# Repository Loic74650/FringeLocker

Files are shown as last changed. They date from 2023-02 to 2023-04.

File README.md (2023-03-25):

# FringeLocker
## Intro
 FringeLocker, as its name indicates, is an electronic system designed to lock interference fringes of an optical interferometer or a holography recording setup.
 The purpose of locking an interferometer is usually to stabilize unstable interference fringes due to mechanical vibrations or thermal drifts.<br />
 Demo video: https://youtu.be/0IrlpE1sPkQ
 
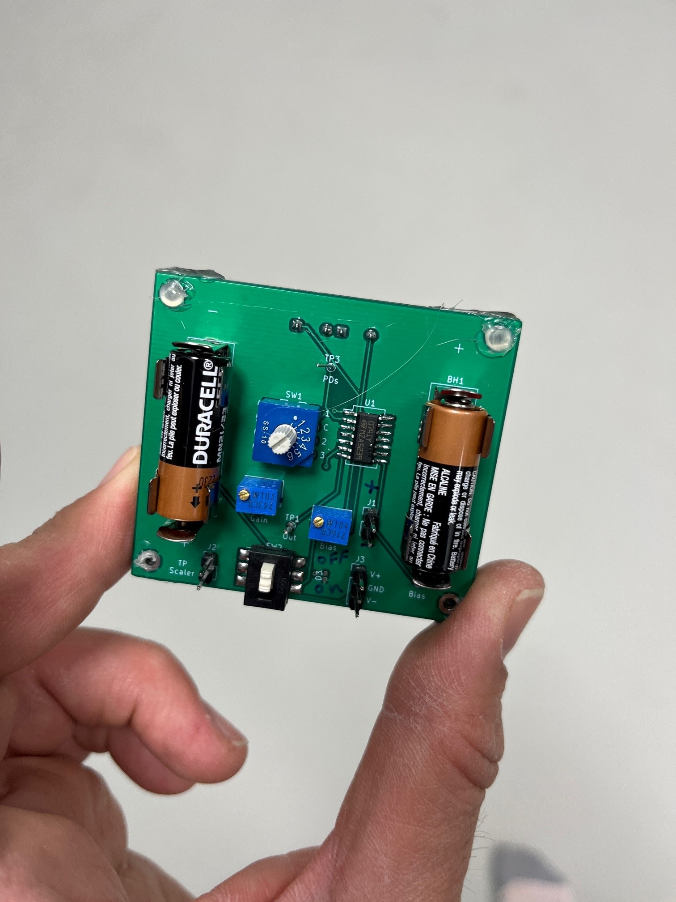
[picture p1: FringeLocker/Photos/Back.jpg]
  <br />
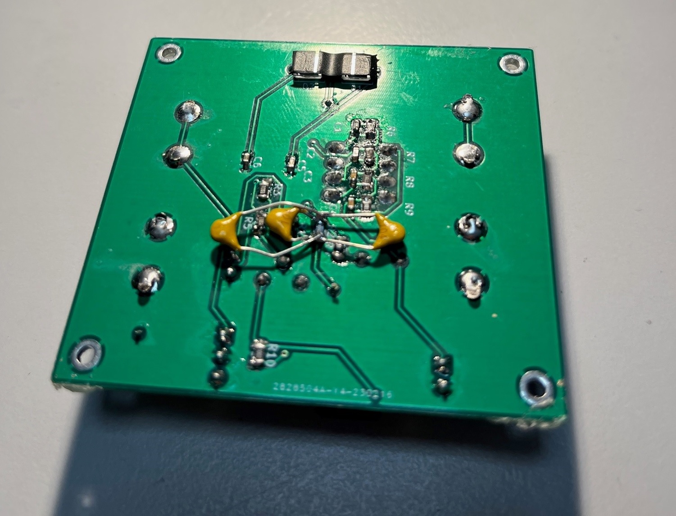
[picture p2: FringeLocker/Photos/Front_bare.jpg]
  <br />
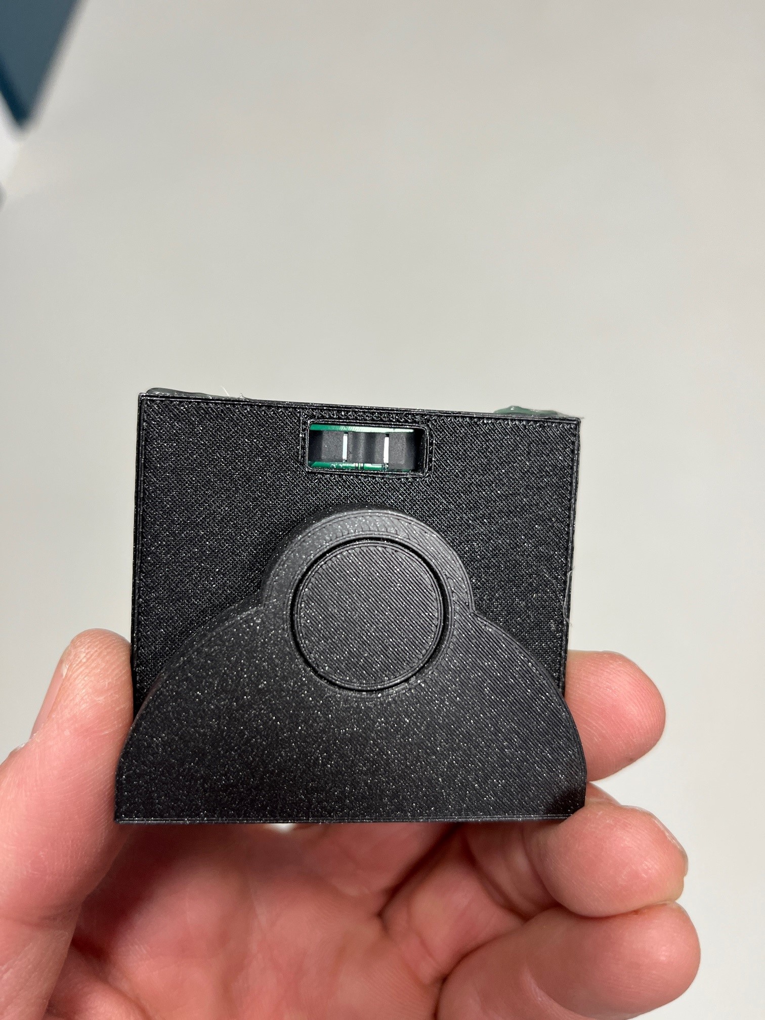
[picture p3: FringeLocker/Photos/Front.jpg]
  <br />
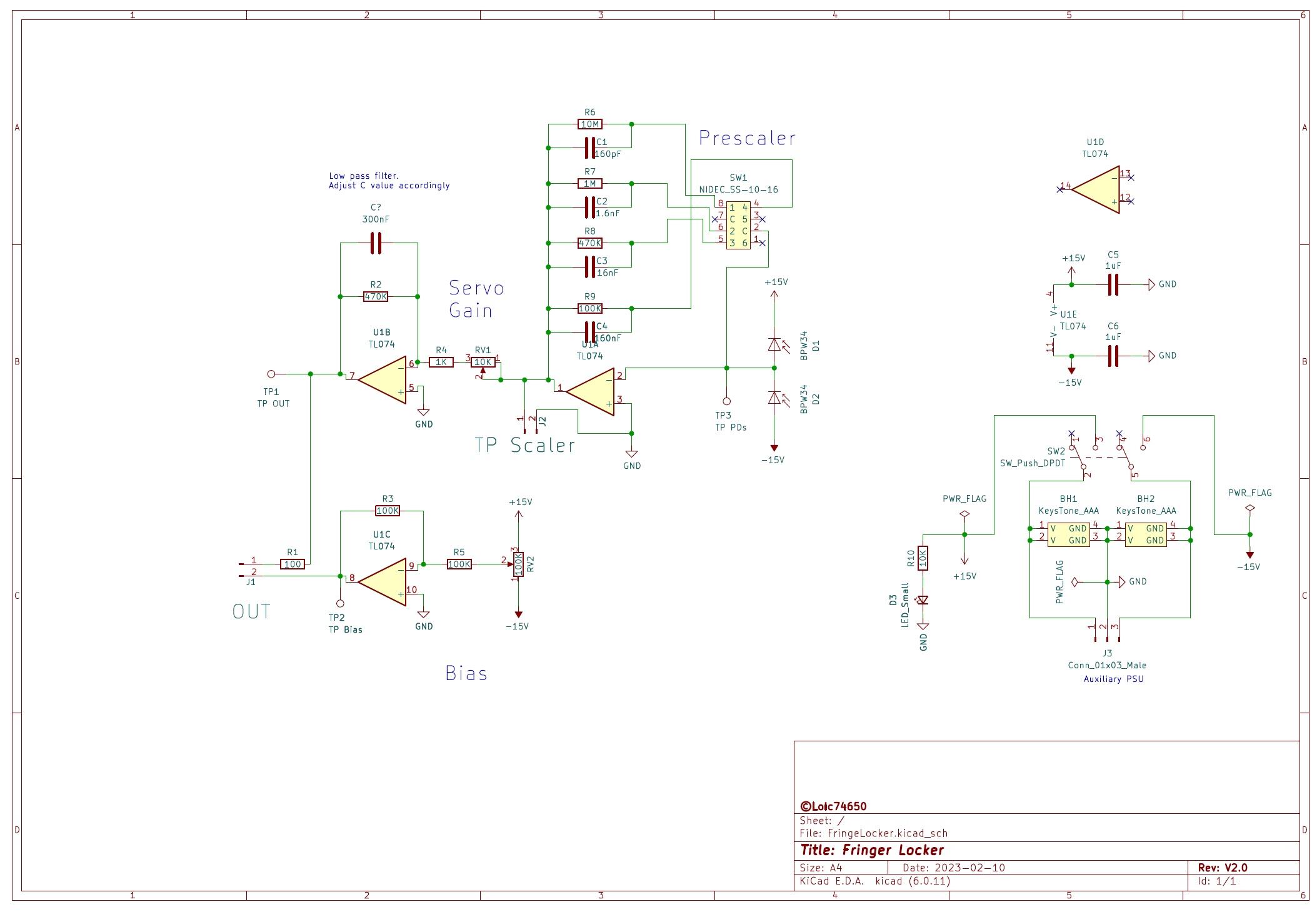
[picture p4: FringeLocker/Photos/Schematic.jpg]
  <br /><br />
 
## Working principle
Two photodiodes sample the interference fringes and detect any movement of those. 
A low noise amplifier and feedback loop drive a mirror which is placed on a piezo transducer in order to move one arm of the interferometer and compensate for the detected fringe movements

## Setup
This version of FringeLocker is powered by two MN21/A23 12V batteries. Alternatively connector J3 on the board can be used to power the board with an external supply of
your choice (remove the batteries first!). The board accepts supply voltages up to +/-18Volts and so currently I am using two 9V batteries in series for each voltage ramp in order to increase lifetime on battery.
The photodiodes need to be masked of, leaving just one slit 0.5mm wide per photodiode. See image in the photos folder.<br />
Slider switch SW2 switched ON/OFF the board.  
There are three adjustments to be performed on the board. 

1- Servo Gain
RV1 10 turns potentiometer adjusts the servo gain. Start by adjusting it to minimum

2- Output bias
RV2 10 turns potentiometer adjusts the level of bias voltage to the piezo transducer. Since positive or negative voltages can be applied to the transducer it is necessary to apply
a bias to it. Use a voltmeter to measure the bias voltage between ground (the pcb mounting holes in each corner are grounded) and Test Point 2 (TP2 or TP Bias) and adjust it to 18 volts or so.

3- PresScaler switch
SW1 is a rotary switch which selects a preamplification of the photodiodes signal with various gains. Start by adjusting it to minimum

## Servo loop adjustment
Place the photodiodes within interference fringes of the interferometer. Adjust the interference fringes spacing so that their spacing is approximately 15mm (twice the spacing between the photodiodes). 
Power the board and start with the lowest gain on the PreScaler switch SW1 and move to larger gains incrementally until the feedback loop starts oscillating.
Revert to the previous gain setting in order to stop the oscillation. You can then fine adjust the loop gain RV1 by increasing it slowly until the loop starts oscillating, then reverting a bit to stop the oscillation.

## Bugs
An unpolarized 100nF capacitor needs to be manually added in parallel with R2 in order to create an active low pass filter and prevent the feedback loop from oscillating

## Credits
Thanks to Phil Hobbs for his help on the schematic design

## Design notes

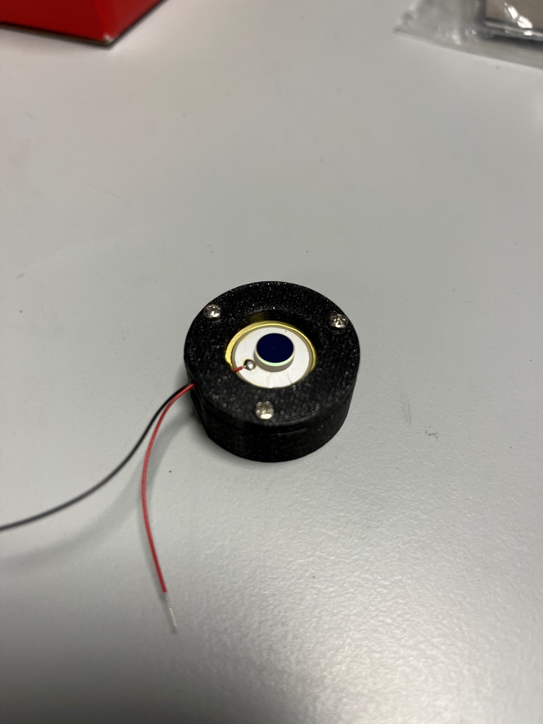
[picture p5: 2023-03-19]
FringeLocker/Photos/FL_6.jpg

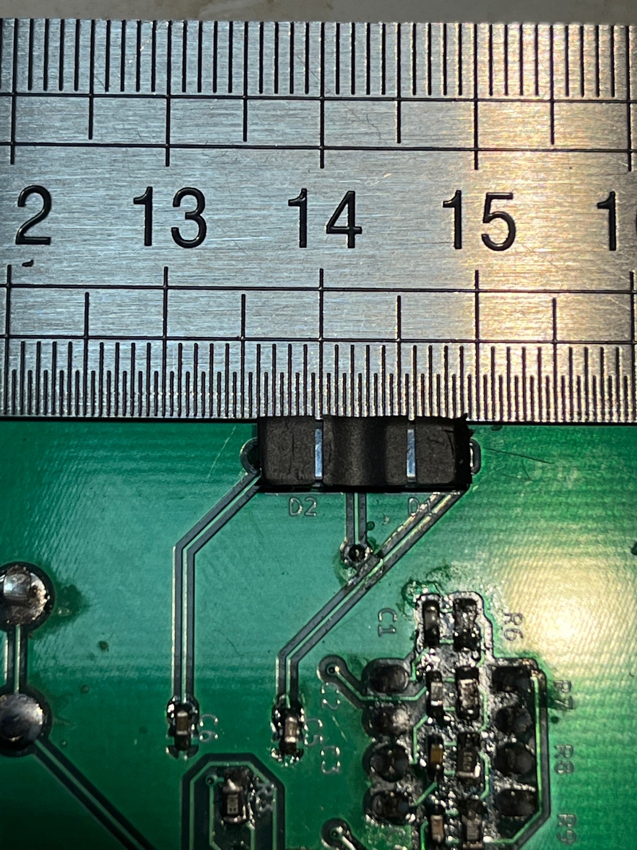
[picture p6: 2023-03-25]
FringeLocker/Photos/PDs_masks.jpg

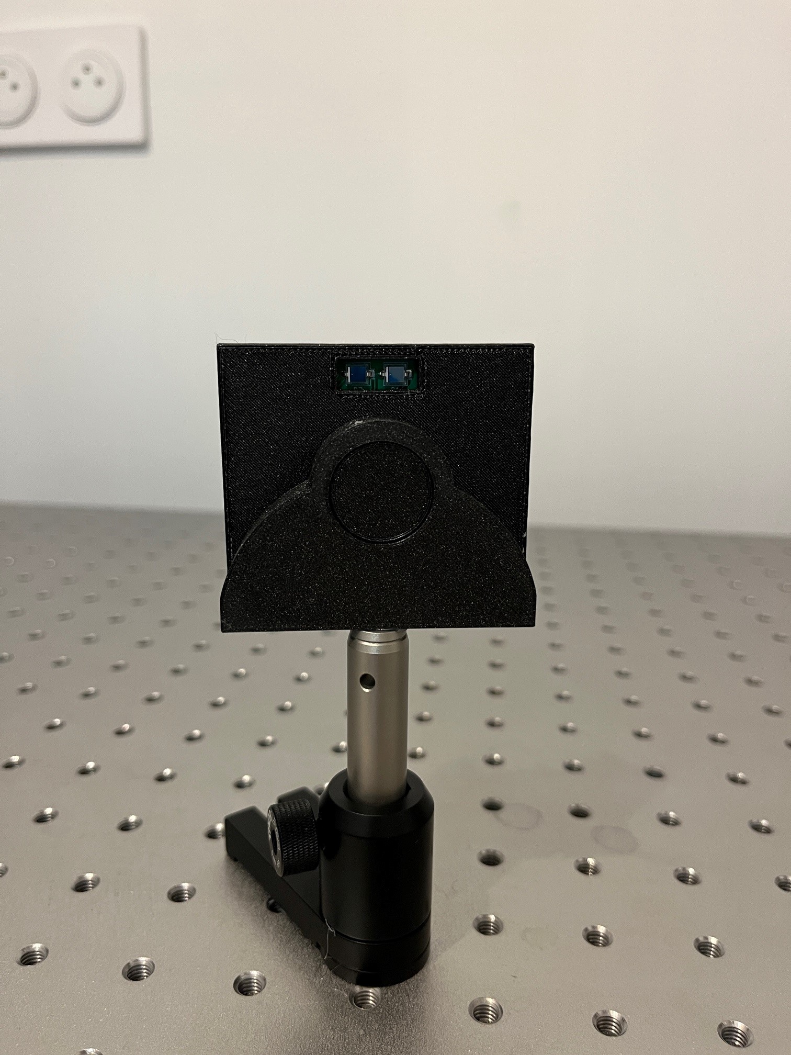
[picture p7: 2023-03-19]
FringeLocker/Photos/FL_1.jpg

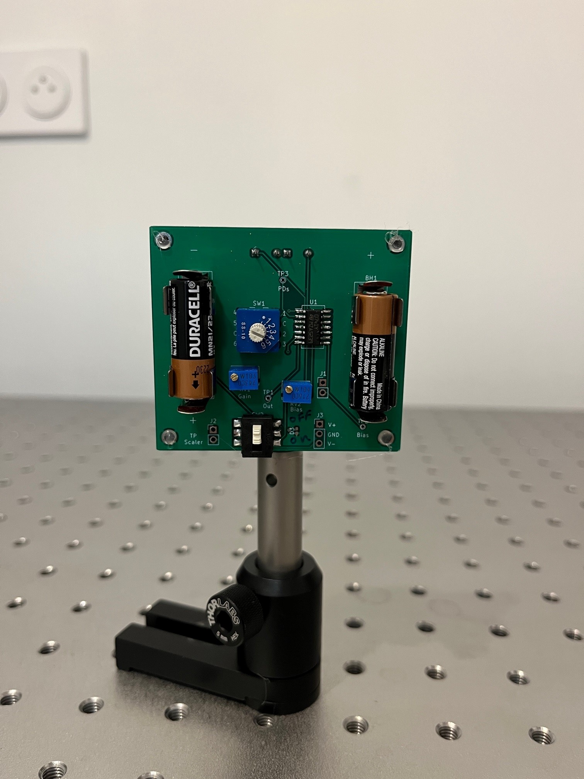
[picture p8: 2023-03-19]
FringeLocker/Photos/FL_2.jpg

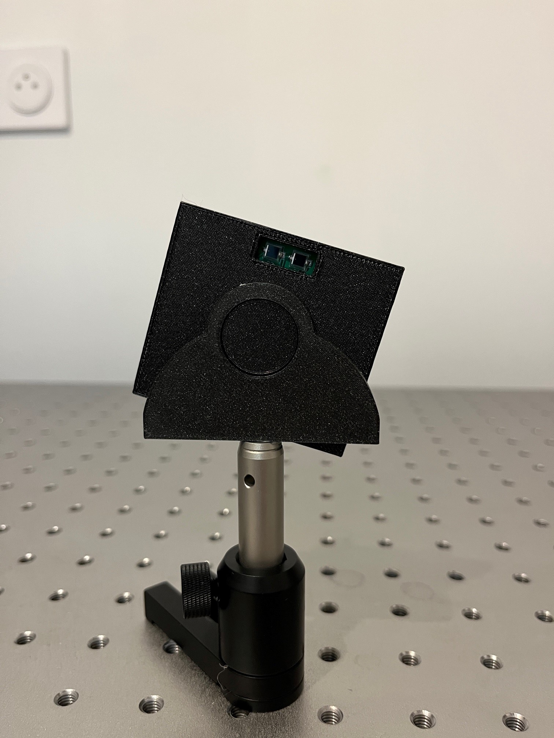
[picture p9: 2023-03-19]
FringeLocker/Photos/FL_3.jpg

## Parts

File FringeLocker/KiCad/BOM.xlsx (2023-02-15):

Column1 | Column2 | Column3 | Column4 | Column5 | Column6 | Column7 | Column8 | Column10
Source: | C:\Users\USER\Documents\GitHub\FringeLocker\FringeLocker\FringeLocker.kicad_sch
Date: | 15/02/2023 15:58:59
Tool: | Eeschema (6.0.11)
Generator: | C:\Program Files\KiCad\6.0\bin\scripting\plugins/bom_csv_grouped_by_value.py
Component Count: | 32
Individual Components:
Item | Qty | Reference(s) | Value | LibPart | Footprint | Datasheet | Unit price (€) | Total price (€)
 |  | BH1 | KeysTone_AAA | My_Library:KeysTone_AAA | BatteryHolder:Keystone_AAA
 |  | BH2 | KeysTone_AAA | My_Library:KeysTone_AAA | BatteryHolder:Keystone_AAA
 |  | C1 | 160pF | Device:C | Capacitor_SMD:C_0603_1608Metric_Pad1.08x0.95mm_HandSolder | ~
 |  | C2 | 1.6nF | Device:C | Capacitor_SMD:C_0603_1608Metric_Pad1.08x0.95mm_HandSolder | ~
 |  | C3 | 16nF | Device:C | Capacitor_SMD:C_0603_1608Metric_Pad1.08x0.95mm_HandSolder | ~
 |  | C4 | 160nF | Device:C | Capacitor_SMD:C_0603_1608Metric_Pad1.08x0.95mm_HandSolder | ~
 |  | C5 | 1uF | Device:C | Capacitor_SMD:C_0603_1608Metric_Pad1.08x0.95mm_HandSolder | ~
 |  | C6 | 1uF | Device:C | Capacitor_SMD:C_0603_1608Metric_Pad1.08x0.95mm_HandSolder | ~
 |  | D1 | BPW34 | Sensor_Optical:BPW34 | OptoDevice:Osram_DIL2_4.3x4.65mm_P5.08mm | http://www.vishay.com/docs/81521/bpw34.pdf
 |  | D2 | BPW34 | Sensor_Optical:BPW34 | OptoDevice:Osram_DIL2_4.3x4.65mm_P5.08mm | http://www.vishay.com/docs/81521/bpw34.pdf
 |  | D3 | LED_Small | Device:LED_Small | LED_SMD:LED_0402_1005Metric_Pad0.77x0.64mm_HandSolder | ~
 |  | J1 | OUT | Connector:Conn_01x02_Male | Connector_PinHeader_2.54mm:PinHeader_1x02_P2.54mm_Vertical | ~
 |  | J2 | TP Scaler | Connector:Conn_01x02_Male | Connector_PinHeader_2.54mm:PinHeader_1x02_P2.54mm_Vertical | ~
 |  | J3 | Conn_01x03_Male | Connector:Conn_01x03_Male | Connector_PinHeader_2.54mm:PinHeader_1x03_P2.54mm_Vertical | ~
 |  | R1 | 100 | Device:R | Resistor_SMD:R_0805_2012Metric_Pad1.20x1.40mm_HandSolder | ~
 |  | R2 | 22K | Device:R | Resistor_SMD:R_0805_2012Metric_Pad1.20x1.40mm_HandSolder | ~
 |  | R3 | 100K | Device:R | Resistor_SMD:R_0805_2012Metric_Pad1.20x1.40mm_HandSolder | ~
 |  | R4 | 1K | Device:R | Resistor_SMD:R_0805_2012Metric_Pad1.20x1.40mm_HandSolder | ~
 |  | R5 | 100K | Device:R | Resistor_SMD:R_0805_2012Metric_Pad1.20x1.40mm_HandSolder | ~
 |  | R6 | 1M | Device:R | Resistor_SMD:R_0805_2012Metric_Pad1.20x1.40mm_HandSolder | ~
 |  | R7 | 100K | Device:R | Resistor_SMD:R_0805_2012Metric_Pad1.20x1.40mm_HandSolder | ~
 |  | R8 | 10K | Device:R | Resistor_SMD:R_0805_2012Metric_Pad1.20x1.40mm_HandSolder | ~
 |  | R9 | 1K | Device:R | Resistor_SMD:R_0805_2012Metric_Pad1.20x1.40mm_HandSolder | ~
 |  | R10 | 10K | Device:R | Resistor_SMD:R_0805_2012Metric_Pad1.20x1.40mm_HandSolder | ~
 |  | RV1 | 10K | FringeLocker-rescue:R_POT-Device | Potentiometer_THT:Potentiometer_Bourns_3266W_Vertical
 |  | RV2 | 100K | FringeLocker-rescue:R_POT-Device | Potentiometer_THT:Potentiometer_Bourns_3266W_Vertical
 |  | SW1 | NIDEC_SS-10-16 | My_Library:NIDEC_SS-10-16 | BatteryHolder:NIDEC_SS-10-16
 |  | SW2 | SW_Push_DPDT | Switch:SW_Push_DPDT | BatteryHolder:SlideSwitchASE_DPDT | ~
 |  | TP1 | TP OUT | Connector:TestPoint | TestPoint:TestPoint_THTPad_D1.0mm_Drill0.5mm | ~
 |  | TP2 | TP Bias | Connector:TestPoint | TestPoint:TestPoint_THTPad_D1.0mm_Drill0.5mm | ~
 |  | TP3 | TP PDs | Connector:TestPoint | TestPoint:TestPoint_THTPad_D1.0mm_Drill0.5mm | ~
 |  | U1 | TL074 | Amplifier_Operational:TL074 | Package_SO:SO-14_5.3x10.2mm_P1.27mm | http://www.ti.com/lit/ds/symlink/tl071.pdf
Collated Components:
Item | Qty | Reference(s) | Value | LibPart | Footprint | Datasheet | Unit price (€) | Total price (€)
1 | 2 | BH1, BH2 | KeysTone_AAA | My_Library:KeysTone_AAA | BatteryHolder:Keystone_AAA |  | 0.38 | 0.76
2 | 1 | C1 | 160pF | Device:C | Capacitor_SMD:C_0603_1608Metric_Pad1.08x0.95mm_HandSolder | ~ | 0.1 | 0.1
3 | 1 | C2 | 1.6nF | Device:C | Capacitor_SMD:C_0603_1608Metric_Pad1.08x0.95mm_HandSolder | ~ | 0.1 | 0.1
4 | 1 | C3 | 16nF | Device:C | Capacitor_SMD:C_0603_1608Metric_Pad1.08x0.95mm_HandSolder | ~ | 0.1 | 0.1
5 | 1 | C4 | 160nF | Device:C | Capacitor_SMD:C_0603_1608Metric_Pad1.08x0.95mm_HandSolder | ~ | 0.1 | 0.1
6 | 2 | C5, C6 | 1uF | Device:C | Capacitor_SMD:C_0603_1608Metric_Pad1.08x0.95mm_HandSolder | ~ | 0.1 | 0.2
7 | 2 | D1, D2 | BPW34 | Sensor_Optical:BPW34 | OptoDevice:Osram_DIL2_4.3x4.65mm_P5.08mm | http://www.vishay.com/docs/81521/bpw34.pdf | 0.68 | 1.36
8 | 1 | D3 | LED_Small | Device:LED_Small | LED_SMD:LED_0402_1005Metric_Pad0.77x0.64mm_HandSolder | ~ | 0.43 | 0.43
9 | 1 | J1 | OUT | Connector:Conn_01x02_Male | Connector_PinHeader_2.54mm:PinHeader_1x02_P2.54mm_Vertical | ~ | 0.1 | 0.1
10 | 1 | J2 | TP Scaler | Connector:Conn_01x02_Male | Connector_PinHeader_2.54mm:PinHeader_1x02_P2.54mm_Vertical | ~ | 0.1 | 0.1
11 | 1 | J3 | Conn_01x03_Male | Connector:Conn_01x03_Male | Connector_PinHeader_2.54mm:PinHeader_1x03_P2.54mm_Vertical | ~ | 0.1 | 0.1
12 | 1 | R1 | 100 | Device:R | Resistor_SMD:R_0805_2012Metric_Pad1.20x1.40mm_HandSolder | ~ | 0.1 | 0.1
13 | 1 | R2 | 22K | Device:R | Resistor_SMD:R_0805_2012Metric_Pad1.20x1.40mm_HandSolder | ~ | 0.1 | 0.1
14 | 3 | R3, R5, R7 | 100K | Device:R | Resistor_SMD:R_0805_2012Metric_Pad1.20x1.40mm_HandSolder | ~ | 0.1 | 0.3
15 | 2 | R4, R9 | 1K | Device:R | Resistor_SMD:R_0805_2012Metric_Pad1.20x1.40mm_HandSolder | ~ | 0.1 | 0.2
16 | 1 | R6 | 1M | Device:R | Resistor_SMD:R_0805_2012Metric_Pad1.20x1.40mm_HandSolder | ~ | 0.1 | 0.1
17 | 2 | R8, R10 | 10K | Device:R | Resistor_SMD:R_0805_2012Metric_Pad1.20x1.40mm_HandSolder | ~ | 0.1 | 0.2
18 | 1 | RV1 | 10K | FringeLocker-rescue:R_POT-Device | Potentiometer_THT:Potentiometer_Bourns_3266W_Vertical |  | 2.49 | 2.49
19 | 1 | RV2 | 100K | FringeLocker-rescue:R_POT-Device | Potentiometer_THT:Potentiometer_Bourns_3266W_Vertical |  | 4.19 | 4.19
20 | 1 | SW1 | NIDEC_SS-10-16 | My_Library:NIDEC_SS-10-16 | BatteryHolder:NIDEC_SS-10-16 |  | 3.88 | 3.88
21 | 1 | SW2 | SW_Push_DPDT | Switch:SW_Push_DPDT | BatteryHolder:SlideSwitchASE_DPDT | ~ | 5.03 | 5.03
22 | 1 | TP1 | TP OUT | Connector:TestPoint | TestPoint:TestPoint_THTPad_D1.0mm_Drill0.5mm | ~ | 0 | 0
23 | 1 | TP2 | TP Bias | Connector:TestPoint | TestPoint:TestPoint_THTPad_D1.0mm_Drill0.5mm | ~ | 0 | 0
24 | 1 | TP3 | TP PDs | Connector:TestPoint | TestPoint:TestPoint_THTPad_D1.0mm_Drill0.5mm | ~ | 0 | 0
25 | 1 | U1 | TL074 | Amplifier_Operational:TL074 | Package_SO:SO-14_5.3x10.2mm_P1.27mm | http://www.ti.com/lit/ds/symlink/tl071.pdf | 0.84 | 0.84
 |  |  |  |  |  |  |  | 0
 |  |  |  |  |  |  |  | 0
 |  |  |  |  |  |  |  | 0
 | 1 | PCB |  | JLCPCB |  | JLPCB | 5 | 5
 |  |  |  |  |  |  | TOTAL | 25.88

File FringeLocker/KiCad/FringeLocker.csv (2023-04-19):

Source: | C:\Users\USER\Documents\GitHub\FringeLocker\FringeLocker\KiCad\FringeLocker.kicad_sch
Date: | 19/04/2023 18:29:47
Tool: | Eeschema (6.0.11)
Generator: | C:\Program Files\KiCad\6.0\bin\scripting\plugins/bom_csv_grouped_by_value.py
Component Count: | 32
Individual Components:
Item | Qty | Reference(s) | Value | LibPart | Footprint | Datasheet
 |  | C1 | 1.6nF | Device:C | Capacitor_SMD:C_0603_1608Metric_Pad1.08x0.95mm_HandSolder | ~
 |  | C2 | 10uF | Device:C | Capacitor_SMD:C_0603_1608Metric_Pad1.08x0.95mm_HandSolder | ~
 |  | C3 | 10uF | Device:C | Capacitor_SMD:C_0603_1608Metric_Pad1.08x0.95mm_HandSolder | ~
 |  | C5 | 1uF | Device:C | Capacitor_SMD:C_0603_1608Metric_Pad1.08x0.95mm_HandSolder | ~
 |  | C6 | 1uF | Device:C | Capacitor_SMD:C_0603_1608Metric_Pad1.08x0.95mm_HandSolder | ~
 |  | D1 | BPW34 | Sensor_Optical:BPW34 | OptoDevice:Osram_DIL2_4.3x4.65mm_P5.08mm | http://www.vishay.com/docs/81521/bpw34.pdf
 |  | D2 | BPW34 | Sensor_Optical:BPW34 | OptoDevice:Osram_DIL2_4.3x4.65mm_P5.08mm | http://www.vishay.com/docs/81521/bpw34.pdf
 |  | D3 | LED_Small | Device:LED_Small | LED_SMD:LED_0402_1005Metric_Pad0.77x0.64mm_HandSolder | ~
 |  | J1 | OUT | Connector:Conn_01x02_Male | Connector_PinHeader_2.54mm:PinHeader_1x02_P2.54mm_Vertical | ~
 |  | J2 | TP Scaler | Connector:Conn_01x02_Male | Connector_PinHeader_2.54mm:PinHeader_1x02_P2.54mm_Vertical | ~
 |  | J3 | Conn_01x03_Male | Connector:Conn_01x03_Male | Connector_PinHeader_2.54mm:PinHeader_1x03_P2.54mm_Vertical | ~
 |  | R1 | 100 | Device:R | Resistor_SMD:R_0805_2012Metric_Pad1.20x1.40mm_HandSolder | ~
 |  | R2 | 250K | Device:R | Resistor_SMD:R_0805_2012Metric_Pad1.20x1.40mm_HandSolder | ~
 |  | R3 | 100K | Device:R | Resistor_SMD:R_0805_2012Metric_Pad1.20x1.40mm_HandSolder | ~
 |  | R4 | 1K | Device:R | Resistor_SMD:R_0805_2012Metric_Pad1.20x1.40mm_HandSolder | ~
 |  | R5 | 100K | Device:R | Resistor_SMD:R_0805_2012Metric_Pad1.20x1.40mm_HandSolder | ~
 |  | R6 | 1M | Device:R | Resistor_SMD:R_0805_2012Metric_Pad1.20x1.40mm_HandSolder | ~
 |  | R7 | 200 | Device:R | Resistor_SMD:R_0805_2012Metric_Pad1.20x1.40mm_HandSolder | ~
 |  | R8 | 200 | Device:R | Resistor_SMD:R_0805_2012Metric_Pad1.20x1.40mm_HandSolder | ~
 |  | R9 | 10K | Device:R | Resistor_SMD:R_0805_2012Metric_Pad1.20x1.40mm_HandSolder | ~
 |  | R10 | 7.5K | Device:R | Resistor_SMD:R_0805_2012Metric_Pad1.20x1.40mm_HandSolder | ~
 |  | R11 | 1K | Device:R | Resistor_SMD:R_0805_2012Metric_Pad1.20x1.40mm_HandSolder | ~
 |  | RV1 | 3310Y_001_503L | Bourns3310:3310Y | Bourns_3310H:Bourns3310Y
 |  | RV2 | 100K | FringeLocker-rescue:R_POT-Device | Potentiometer_THT:Potentiometer_Bourns_3266W_Vertical
 |  | RV3 | 3310H_001_102L | Bourns3310:Bourns3310H_2 | Bourns_3310H:Bourns3310H
 |  | RV4 | 10K | FringeLocker-rescue:R_POT-Device | Potentiometer_THT:Potentiometer_Bourns_3266W_Vertical
 |  | SW1 | SW_Push_DPDT | Switch:SW_Push_DPDT | BatteryHolder:SlideSwitchASE_DPDT | ~
 |  | TP1 | TP OUT | Connector:TestPoint | TestPoint:TestPoint_THTPad_D1.0mm_Drill0.5mm | ~
 |  | TP2 | TP Bias | Connector:TestPoint | TestPoint:TestPoint_THTPad_D1.0mm_Drill0.5mm | ~
 |  | TP3 | TP PDs | Connector:TestPoint | TestPoint:TestPoint_THTPad_D1.0mm_Drill0.5mm | ~
 |  | U1 | TL074 | Amplifier_Operational:TL074 | Package_SO:SO-14_5.3x10.2mm_P1.27mm | http://www.ti.com/lit/ds/symlink/tl071.pdf
 |  | U2 | TL074 | Amplifier_Operational:TL074 | Package_SO:SO-14_5.3x10.2mm_P1.27mm | http://www.ti.com/lit/ds/symlink/tl071.pdf
Collated Components:
Item | Qty | Reference(s) | Value | LibPart | Footprint | Datasheet
1 | 1 | C1 | 1.6nF | Device:C | Capacitor_SMD:C_0603_1608Metric_Pad1.08x0.95mm_HandSolder | ~
2 | 2 | C2, C3 | 10uF | Device:C | Capacitor_SMD:C_0603_1608Metric_Pad1.08x0.95mm_HandSolder | ~
3 | 2 | C5, C6 | 1uF | Device:C | Capacitor_SMD:C_0603_1608Metric_Pad1.08x0.95mm_HandSolder | ~
4 | 2 | D1, D2 | BPW34 | Sensor_Optical:BPW34 | OptoDevice:Osram_DIL2_4.3x4.65mm_P5.08mm | http://www.vishay.com/docs/81521/bpw34.pdf
5 | 1 | D3 | LED_Small | Device:LED_Small | LED_SMD:LED_0402_1005Metric_Pad0.77x0.64mm_HandSolder | ~
6 | 1 | J1 | OUT | Connector:Conn_01x02_Male | Connector_PinHeader_2.54mm:PinHeader_1x02_P2.54mm_Vertical | ~
7 | 1 | J2 | TP Scaler | Connector:Conn_01x02_Male | Connector_PinHeader_2.54mm:PinHeader_1x02_P2.54mm_Vertical | ~
8 | 1 | J3 | Conn_01x03_Male | Connector:Conn_01x03_Male | Connector_PinHeader_2.54mm:PinHeader_1x03_P2.54mm_Vertical | ~
9 | 1 | R1 | 100 | Device:R | Resistor_SMD:R_0805_2012Metric_Pad1.20x1.40mm_HandSolder | ~
10 | 1 | R2 | 250K | Device:R | Resistor_SMD:R_0805_2012Metric_Pad1.20x1.40mm_HandSolder | ~
11 | 2 | R3, R5 | 100K | Device:R | Resistor_SMD:R_0805_2012Metric_Pad1.20x1.40mm_HandSolder | ~
12 | 2 | R4, R11 | 1K | Device:R | Resistor_SMD:R_0805_2012Metric_Pad1.20x1.40mm_HandSolder | ~
13 | 1 | R6 | 1M | Device:R | Resistor_SMD:R_0805_2012Metric_Pad1.20x1.40mm_HandSolder | ~
14 | 2 | R7, R8 | 200 | Device:R | Resistor_SMD:R_0805_2012Metric_Pad1.20x1.40mm_HandSolder | ~
15 | 1 | R9 | 10K | Device:R | Resistor_SMD:R_0805_2012Metric_Pad1.20x1.40mm_HandSolder | ~
16 | 1 | R10 | 7.5K | Device:R | Resistor_SMD:R_0805_2012Metric_Pad1.20x1.40mm_HandSolder | ~
17 | 1 | RV1 | 3310Y_001_503L | Bourns3310:3310Y | Bourns_3310H:Bourns3310Y
18 | 1 | RV2 | 100K | FringeLocker-rescue:R_POT-Device | Potentiometer_THT:Potentiometer_Bourns_3266W_Vertical
19 | 1 | RV3 | 3310H_001_102L | Bourns3310:Bourns3310H_2 | Bourns_3310H:Bourns3310H
20 | 1 | RV4 | 10K | FringeLocker-rescue:R_POT-Device | Potentiometer_THT:Potentiometer_Bourns_3266W_Vertical
21 | 1 | SW1 | SW_Push_DPDT | Switch:SW_Push_DPDT | BatteryHolder:SlideSwitchASE_DPDT | ~
22 | 1 | TP1 | TP OUT | Connector:TestPoint | TestPoint:TestPoint_THTPad_D1.0mm_Drill0.5mm | ~
23 | 1 | TP2 | TP Bias | Connector:TestPoint | TestPoint:TestPoint_THTPad_D1.0mm_Drill0.5mm | ~
24 | 1 | TP3 | TP PDs | Connector:TestPoint | TestPoint:TestPoint_THTPad_D1.0mm_Drill0.5mm | ~
25 | 2 | U1, U2 | TL074 | Amplifier_Operational:TL074 | Package_SO:SO-14_5.3x10.2mm_P1.27mm | http://www.ti.com/lit/ds/symlink/tl071.pdf

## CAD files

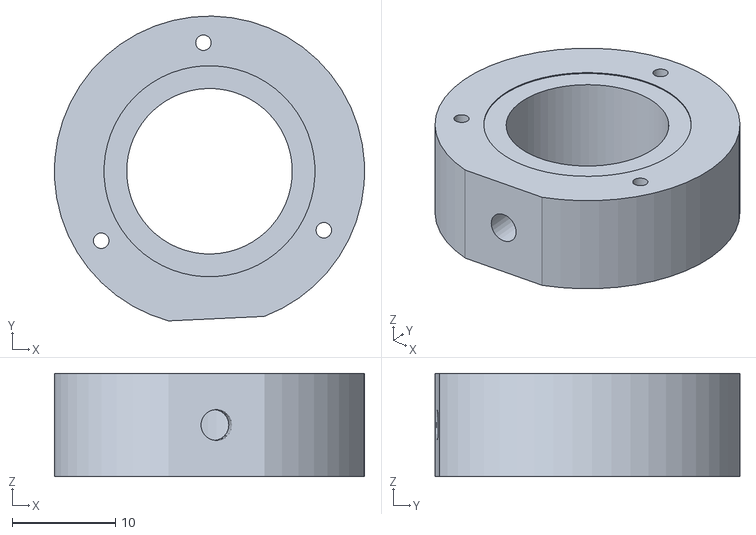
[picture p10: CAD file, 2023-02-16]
FringeLocker/3D Files/SupportPiezoDisc.stl
30.0 x 29.5 x 10.0

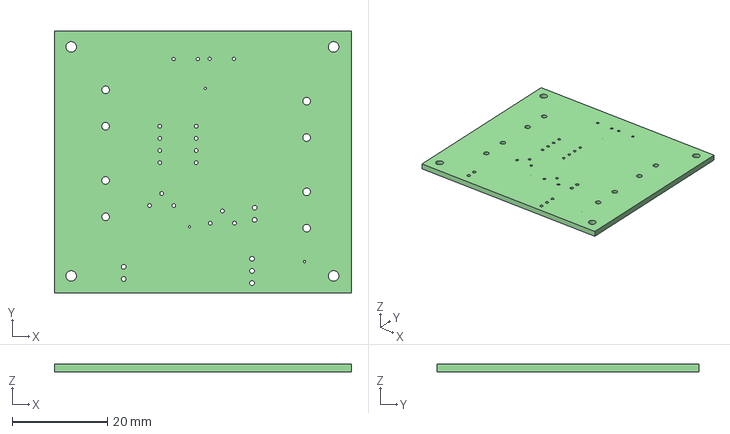
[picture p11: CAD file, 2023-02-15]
FringeLocker/KiCad/FringeLocker.step
62.2 x 54.9 x 1.60 mm

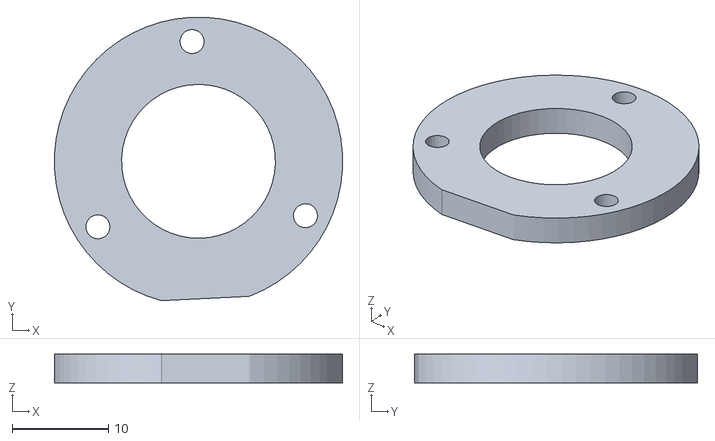
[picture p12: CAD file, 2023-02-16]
FringeLocker/3D Files/ClampPiezoDisc.stl
30.0 x 29.5 x 3.00

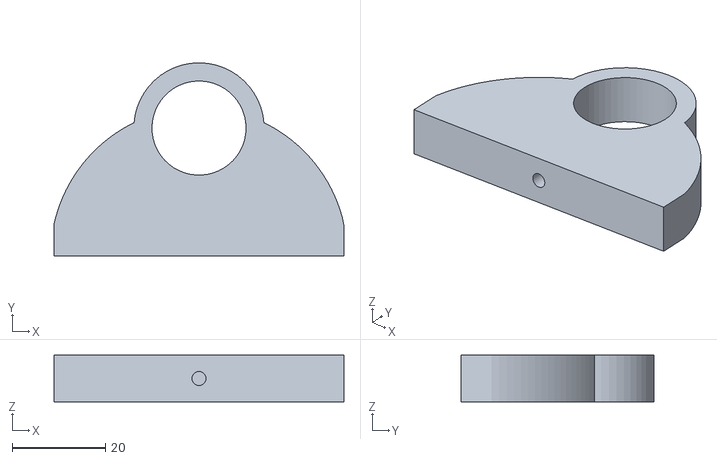
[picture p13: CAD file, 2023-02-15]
FringeLocker/3D Files/SupportPost.stl
62.2 x 41.5 x 10.0

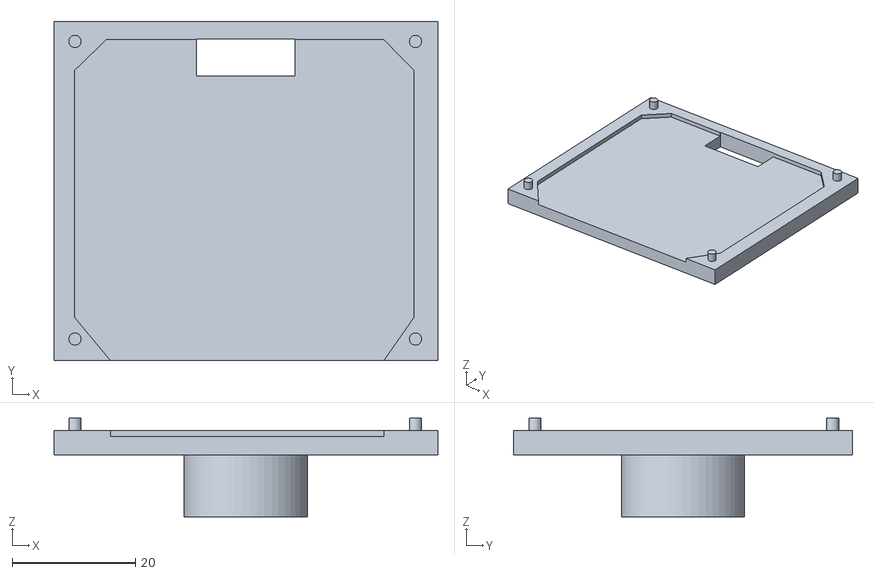
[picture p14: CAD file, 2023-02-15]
FringeLocker/3D Files/SupportPCB.stl
62.2 x 55.0 x 16.0

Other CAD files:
FringeLocker/3D Files/PCBHolderAssembly.skp
FringeLocker/3D Files/PiezoAssembly.skp

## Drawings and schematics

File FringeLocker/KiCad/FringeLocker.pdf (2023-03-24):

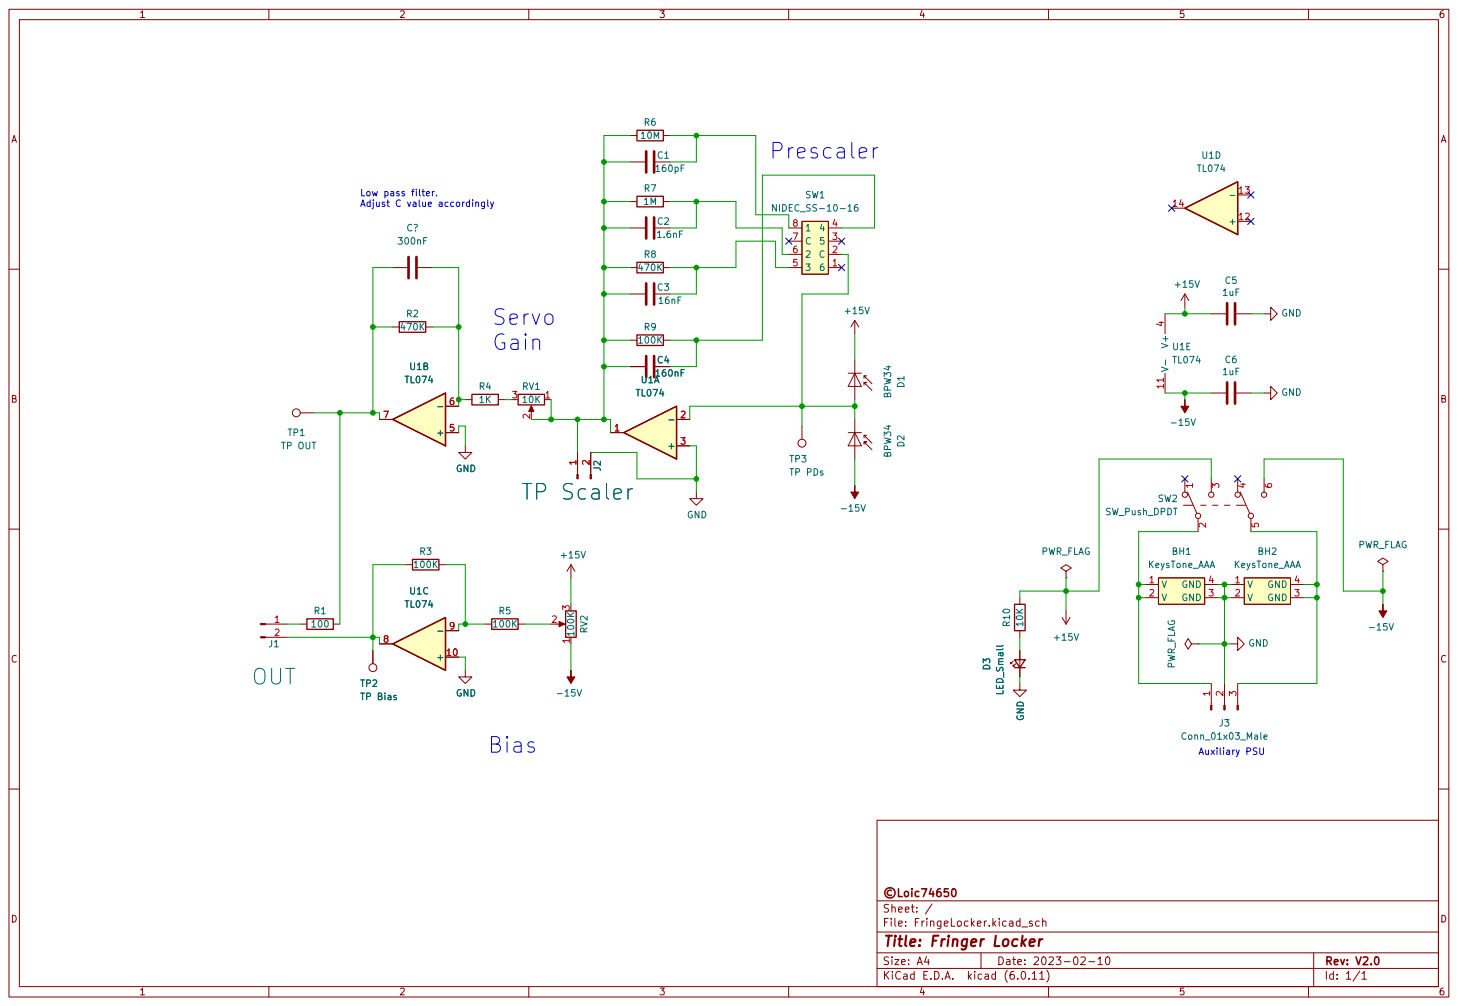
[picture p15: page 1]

Low pass filter. Adjust C value accordingly

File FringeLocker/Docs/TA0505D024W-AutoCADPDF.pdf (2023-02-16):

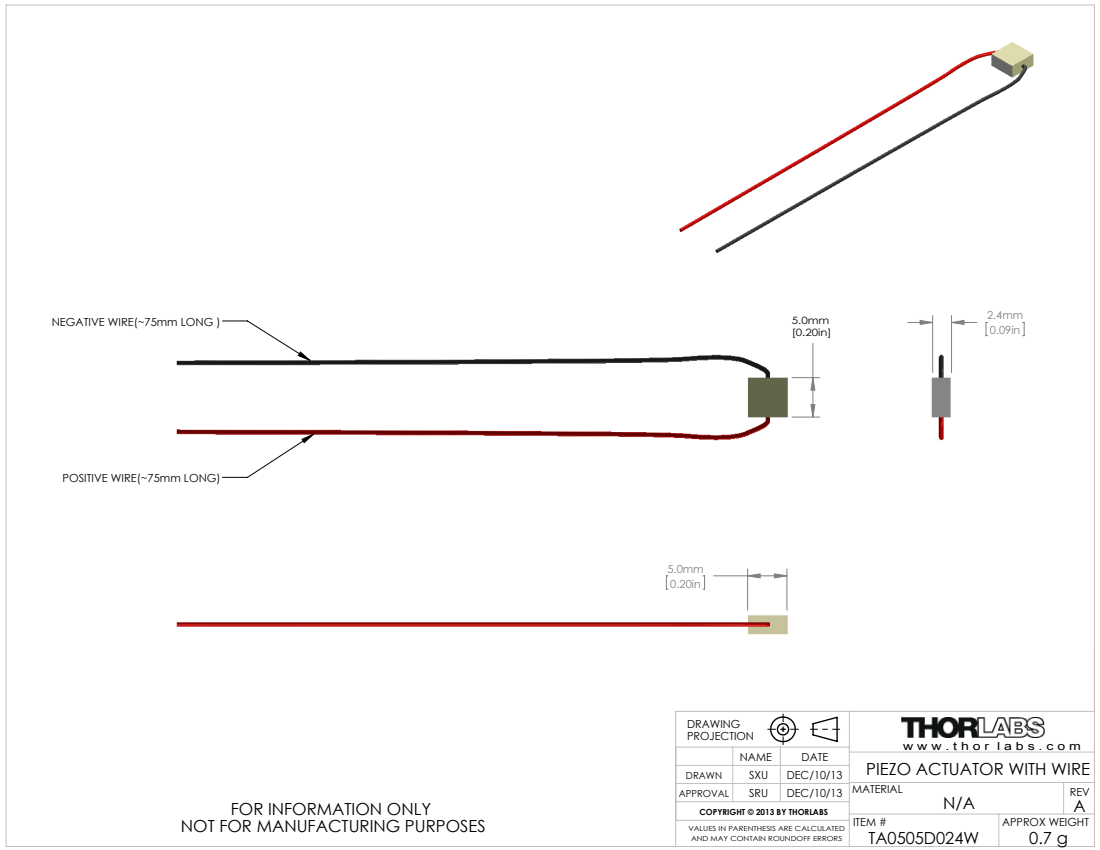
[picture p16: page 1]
NEGATIVE WIRE(~75mm LONG ); ITEM #; APPROX WEIGHT

POSITIVE WIRE(~75mm LONG)

DRAWING PROJECTION | | w w w . t h o r l a b s . c o m

NAME | DATE
APPROVAL | SRU | DEC/10/13 | MATERIAL N/A | REV A

PIEZO ACTUATOR WITH WIRE

DRAWN | SXU | DEC/10/13

FOR INFORMATION ONLY
NOT FOR MANUFACTURING PURPOSES

COPYRIGHT © 2013 BY THORLABS

0.7 g VALUES IN PARENTHESIS ARE CALCULATED
AND MAY CONTAIN ROUNDOFF ERRORS

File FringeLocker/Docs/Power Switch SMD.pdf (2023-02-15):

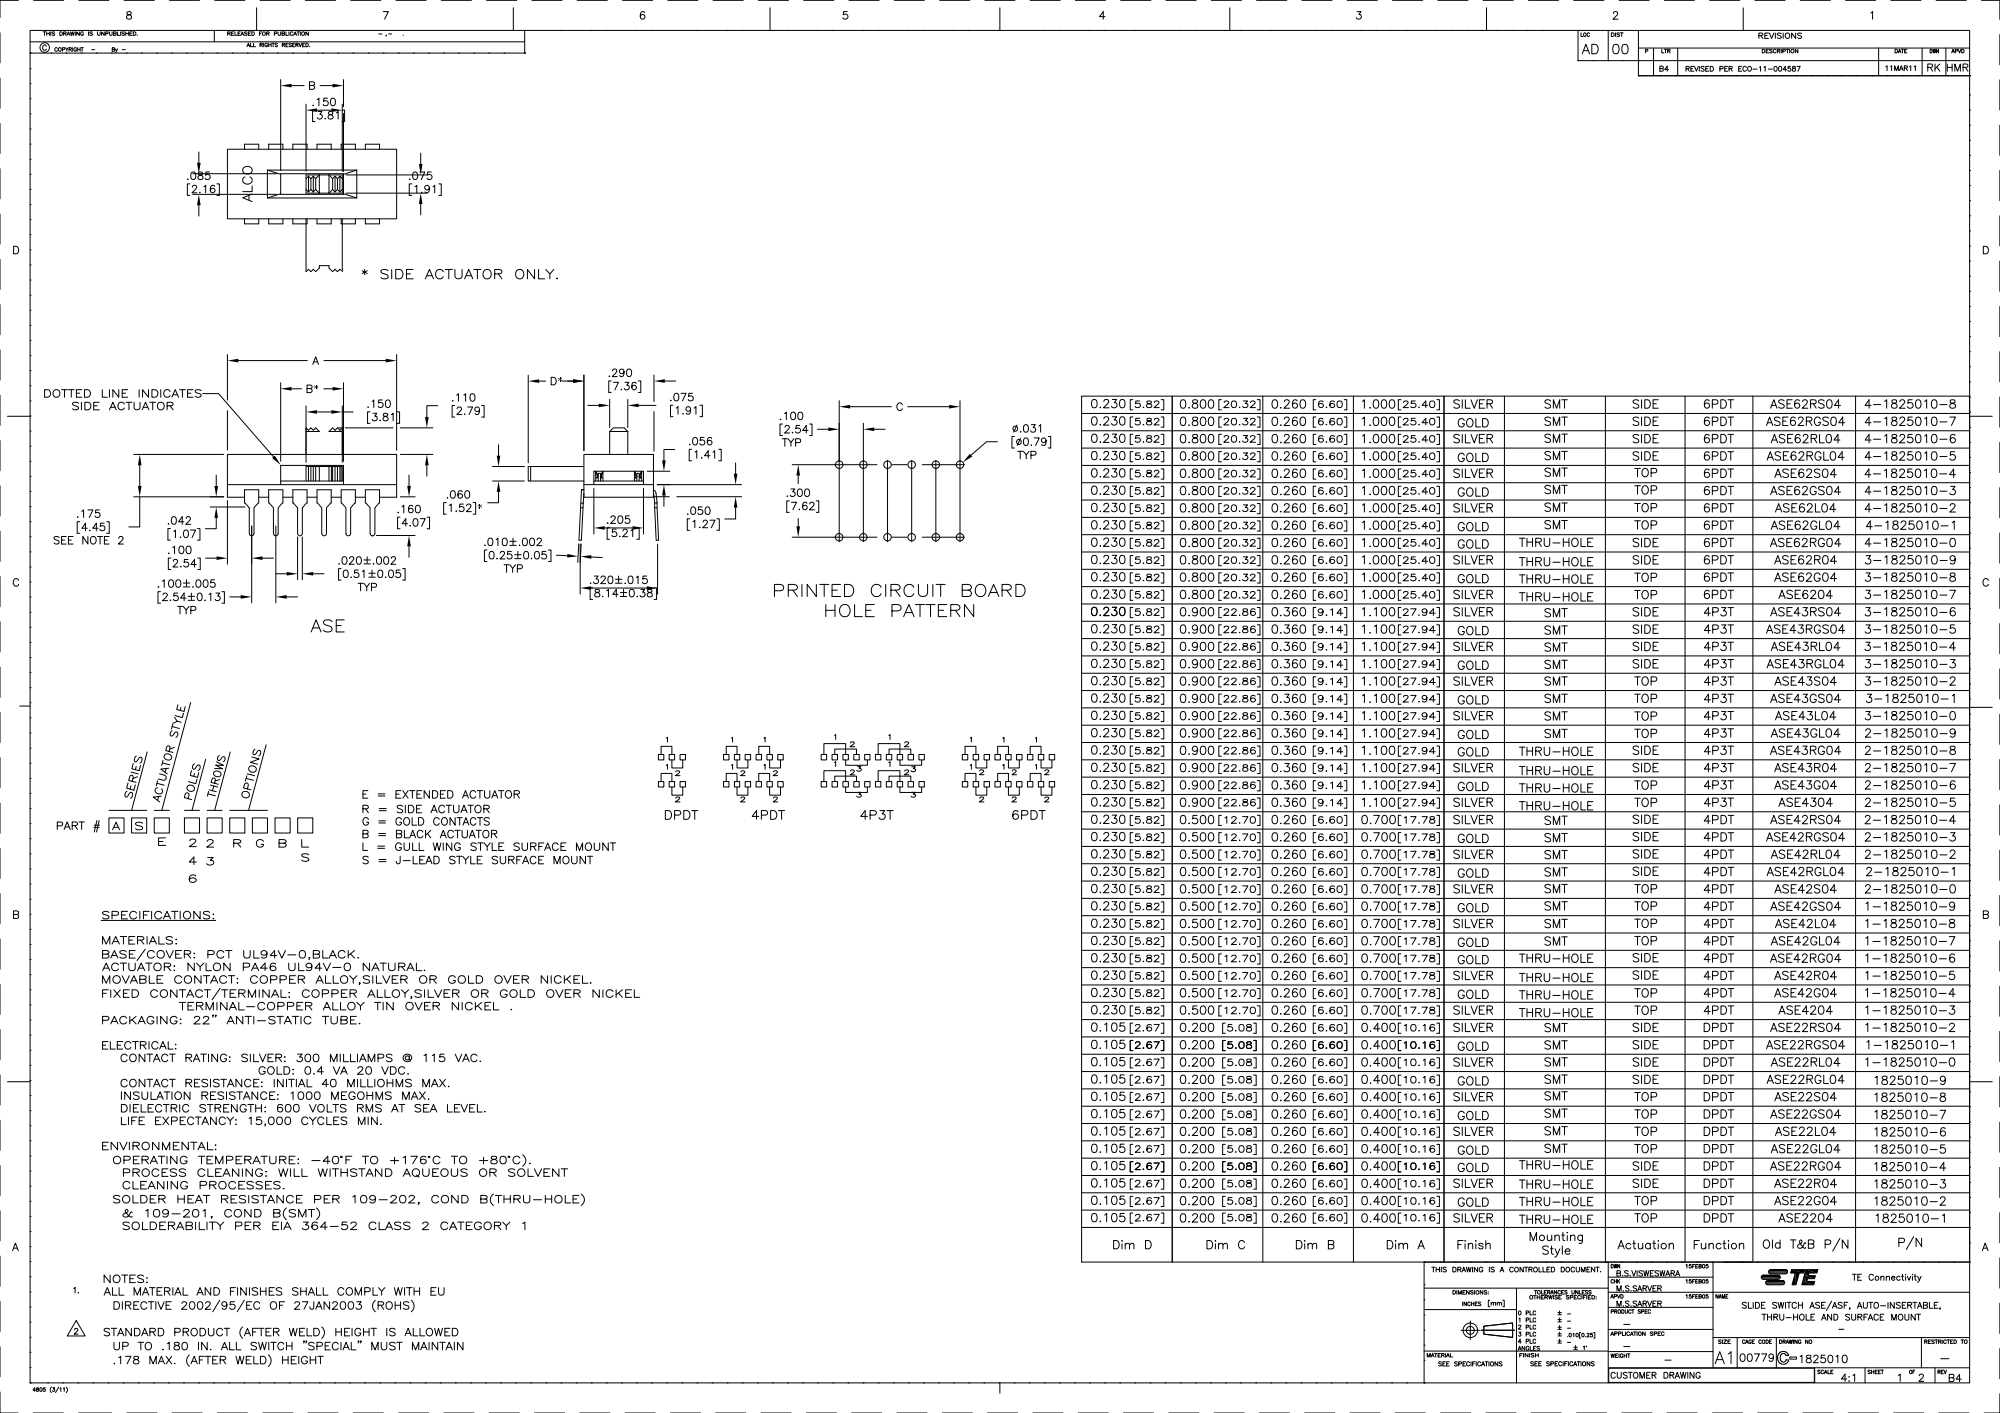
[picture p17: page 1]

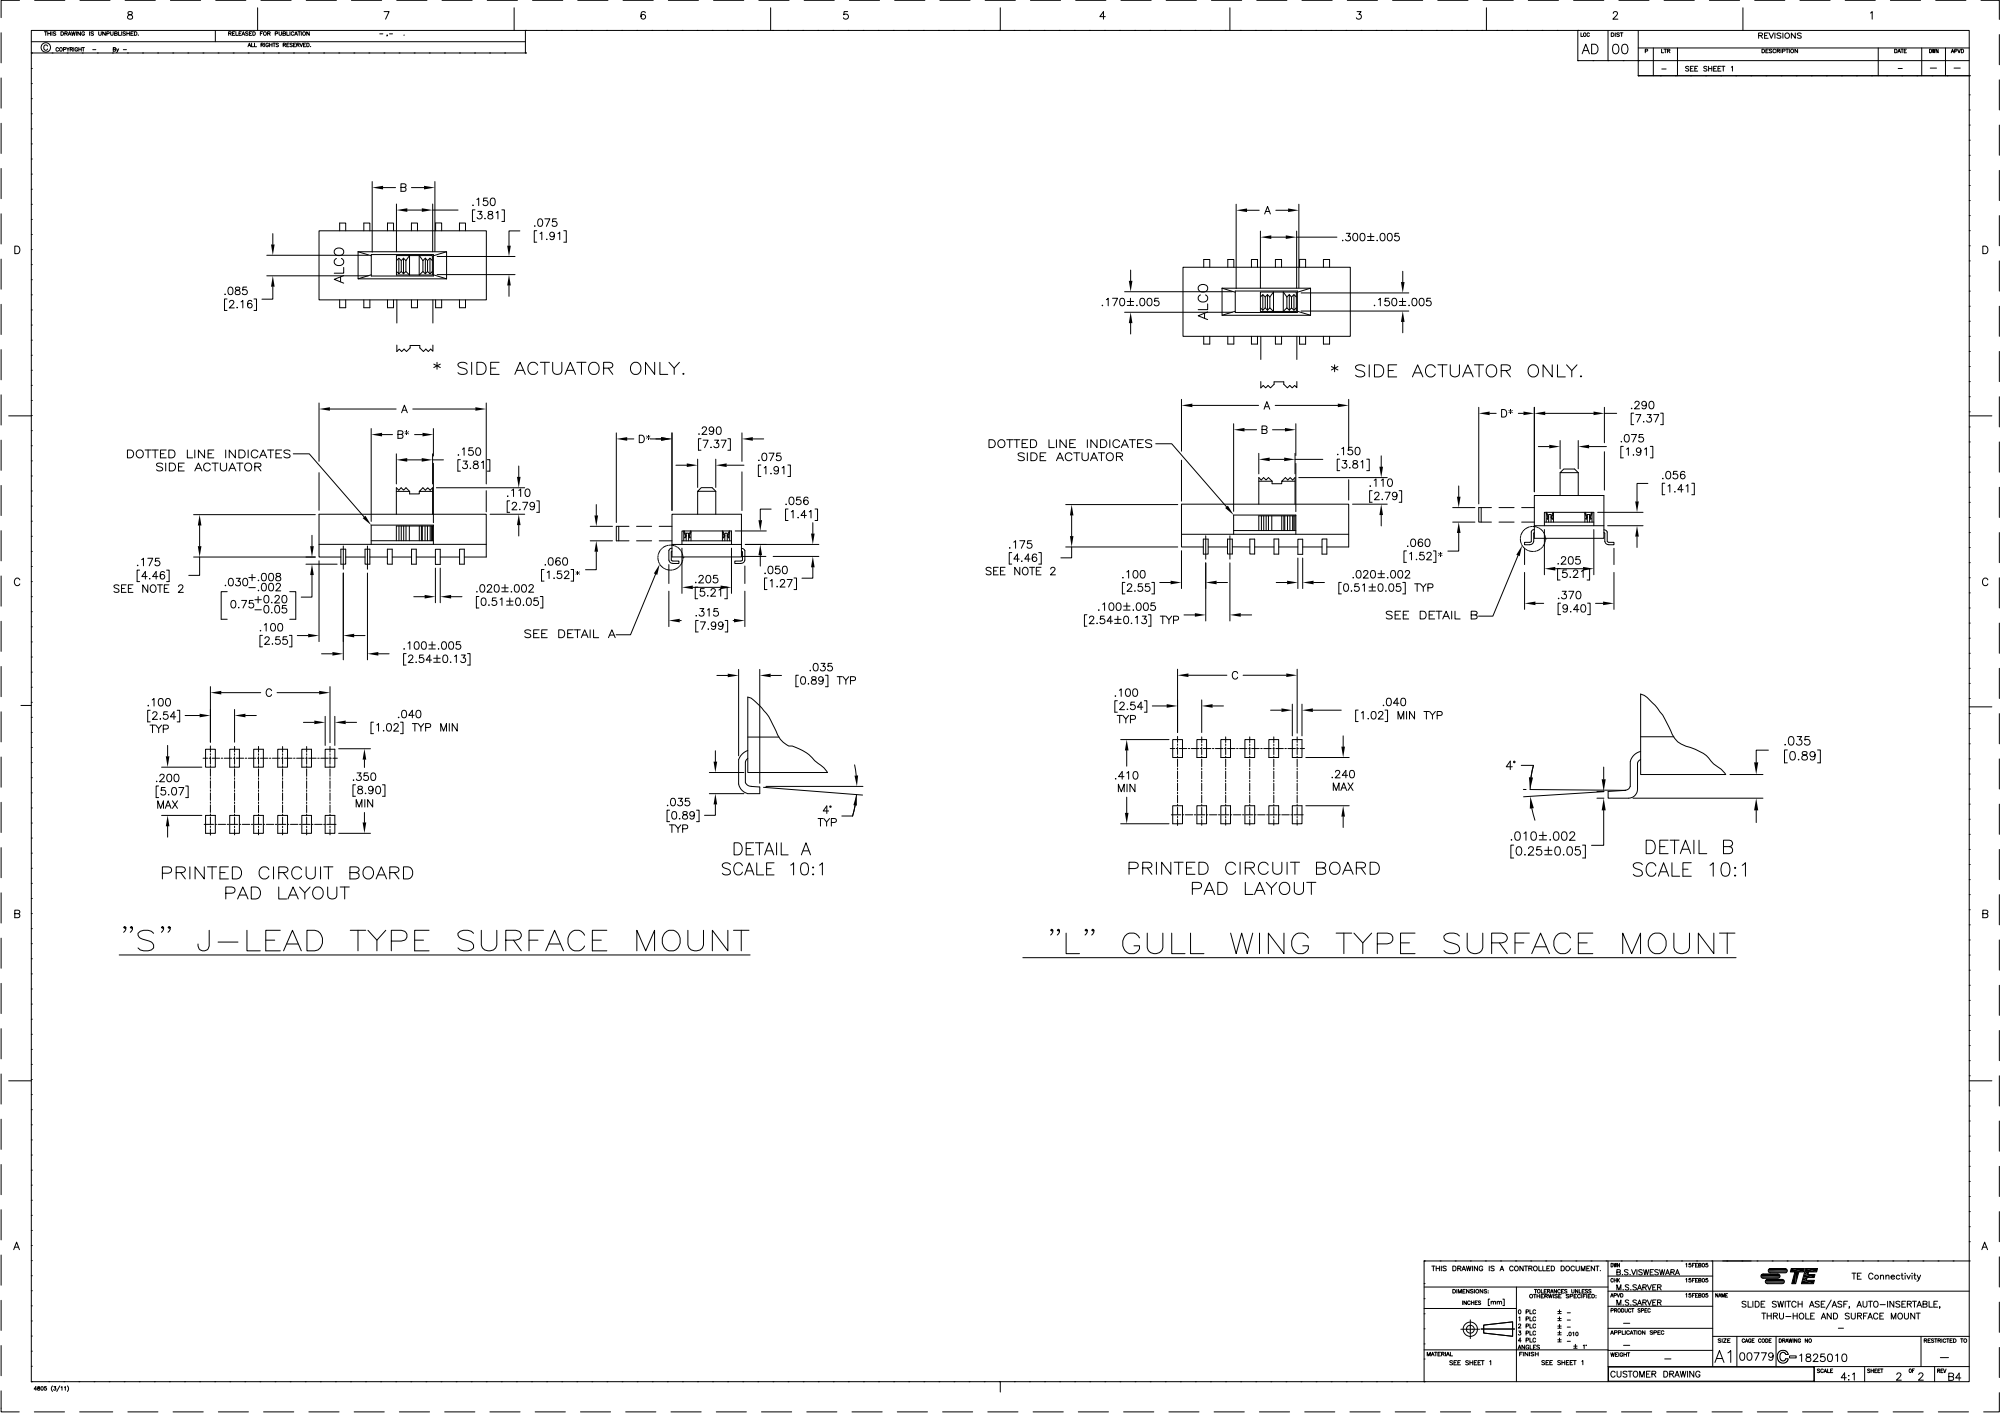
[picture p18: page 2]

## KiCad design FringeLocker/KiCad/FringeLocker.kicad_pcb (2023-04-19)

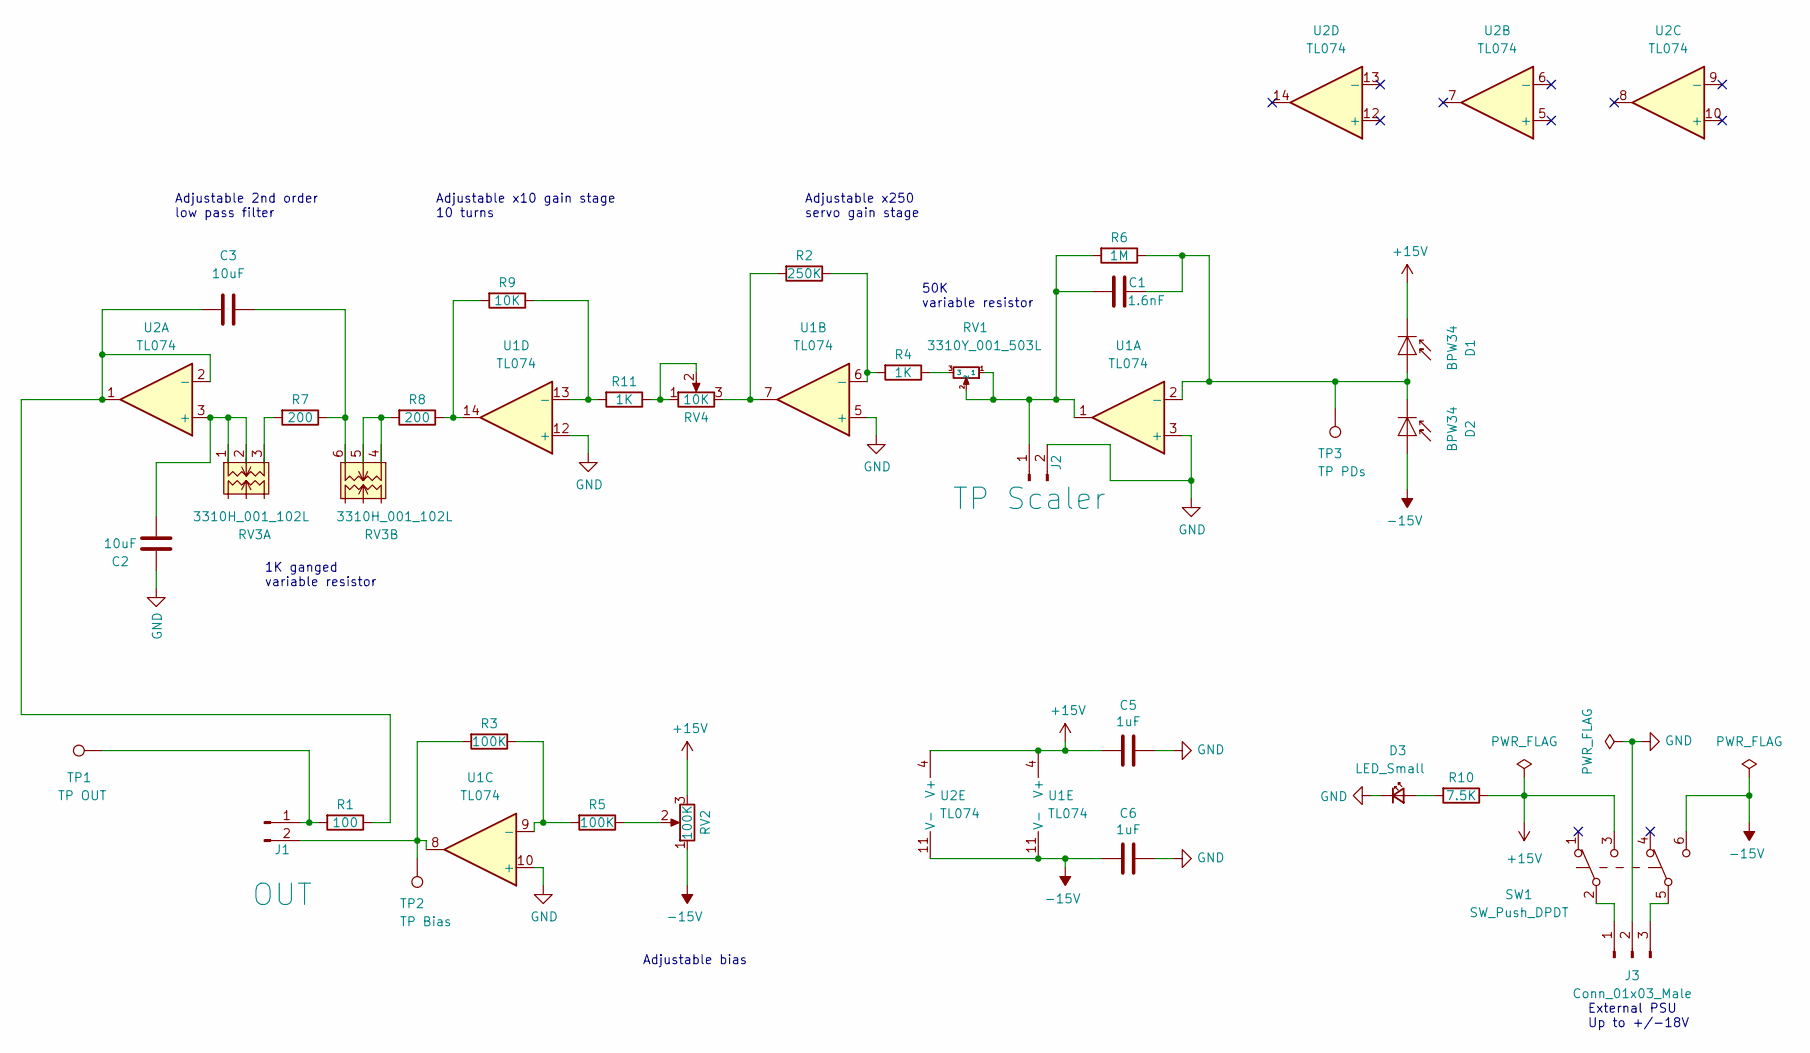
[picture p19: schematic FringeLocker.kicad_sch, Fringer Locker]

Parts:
C1: 1.6nF; C_0603_1608Metric_Pad1.08x0.95mm_HandSolder
C2, C3: 10uF; C_1210_3225Metric_Pad1.33x2.70mm_HandSolder
C5, C6: 1uF; C_0603_1608Metric_Pad1.08x0.95mm_HandSolder
D1, D2: BPW34; Osram_DIL2_4.3x4.65mm_P5.08mm
D3: LED_Small; LED_0805_2012Metric_Pad1.15x1.40mm_HandSolder
J1: OUT; PinHeader_1x02_P2.54mm_Vertical
J2: TP Scaler; PinHeader_1x02_P2.54mm_Vertical
J3: Conn_01x03_Male; PinHeader_1x03_P2.54mm_Vertical
R1: 100; R_0805_2012Metric_Pad1.20x1.40mm_HandSolder
R2: 250K; R_0805_2012Metric_Pad1.20x1.40mm_HandSolder
R3, R5: 100K; R_0805_2012Metric_Pad1.20x1.40mm_HandSolder
R4, R11: 1K; R_0805_2012Metric_Pad1.20x1.40mm_HandSolder
R6: 1M; R_0805_2012Metric_Pad1.20x1.40mm_HandSolder
R7, R8: 200; R_0805_2012Metric_Pad1.20x1.40mm_HandSolder
R9: 10K; R_0805_2012Metric_Pad1.20x1.40mm_HandSolder
R10: 7.5K; R_0805_2012Metric_Pad1.20x1.40mm_HandSolder
RV1: 3310Y_001_503L; Bourns3310Y
RV2: 100K; Potentiometer_Bourns_3266W_Vertical
RV3: 3310H_001_102L; Bourns3310H
RV4: 10K; Potentiometer_Bourns_3266W_Vertical
SW1: SW_Push_DPDT; SlideSwitchASE_DPDT
TP1: TP OUT; TestPoint_THTPad_D1.0mm_Drill0.5mm
TP2: TP Bias; TestPoint_THTPad_D1.0mm_Drill0.5mm
TP3: TP PDs; TestPoint_THTPad_D1.0mm_Drill0.5mm
U1, U2: TL074; SO-14_5.3x10.2mm_P1.27mm

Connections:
+15V: C5.1, D1.1 (K), R10.1, RV2.3, SW1.3 (C), U1.4 (V+), U2.4 (V+)
-15V: C6.1, D2.2 (A), RV2.1, SW1.6 (C), U1.11 (V-), U2.11 (V-)
GND: C2.2, C5.2, C6.2, D3.1 (K), J2.2, J3.2, U1.3 (+), U1.5 (+), U1.10 (+), U1.12 (+); also elsewhere on the board
unnamed: C1.1, J2.1, R6.2, RV1.1, RV1.2, U1.1
unnamed: C1.2, D1.2 (A), D2.1 (K), R6.1, TP3.1, U1.2 (-)
unnamed: C2.1, RV3.1 (A), RV3.2 (B), U2.3 (+)
unnamed: C3.1, R7.1, RV3.6 (F)
unnamed: C3.2, R1.1, U2.1, U2.2 (-)
unnamed: D3.2 (A), R10.2
unnamed: J1.1, R1.2, TP1.1
unnamed: J1.2, R3.2, TP2.1, U1.8
unnamed: J3.1, SW1.2 (B)
unnamed: J3.3, SW1.5 (B)
unnamed: R2.1, R4.2, U1.6 (-)
unnamed: R2.2, RV4.3, U1.7
unnamed: R3.1, R5.2, U1.9 (-)
unnamed: R4.1, RV1.3
unnamed: R5.1, RV2.2
unnamed: R7.2, RV3.3 (C)
unnamed: R8.1, R9.2, U1.14
unnamed: R8.2, RV3.4 (D), RV3.5 (E)
unnamed: R11.1, RV4.1, RV4.2
unnamed: R9.1, R11.2, U1.13 (-)

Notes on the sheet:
External PSU Up to +/-18V
Adjustable x10 gain stage 10 turns
Adjustable x250 servo gain stage
1K ganged variable resistor
Adjustable 2nd order low pass filter
50K variable resistor
Adjustable bias

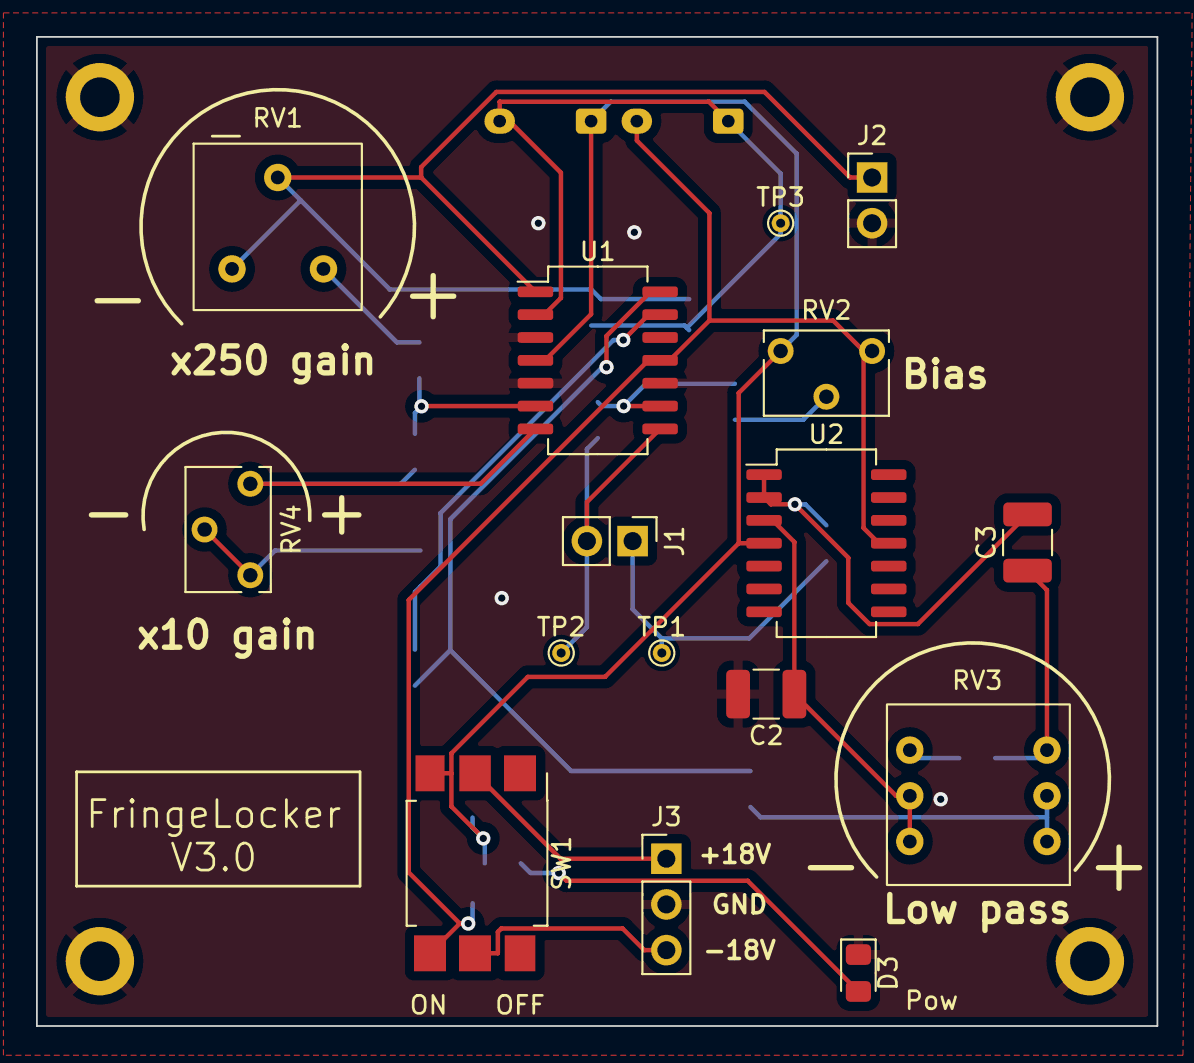
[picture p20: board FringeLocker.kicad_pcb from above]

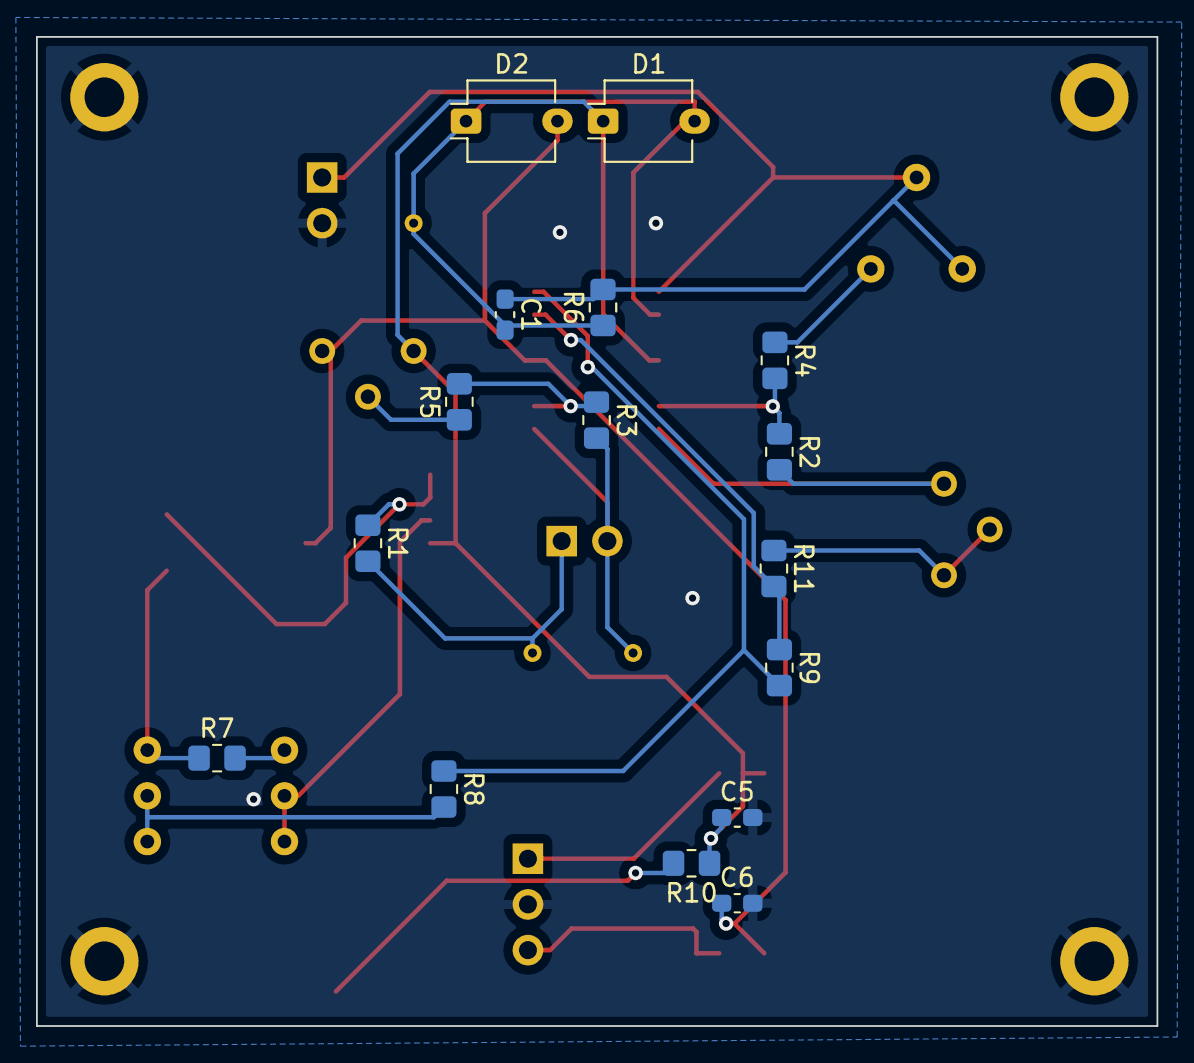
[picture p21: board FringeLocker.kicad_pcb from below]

Board: 2 copper layers, 62.2 x 54.9 mm, 36 parts (16 on the bottom side), 23 nets.

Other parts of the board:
REF1, REF2, REF3, REF4: MountingHole_2.2mm_M2_DIN965_Pad

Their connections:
GND: REF1.1, REF2.1, REF3.1, REF4.1; also elsewhere on the board

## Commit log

2023-02-10 started PCB
    [FringeLocker.csv, FringeLocker.dsn, FringeLocker.kicad_pcb, FringeLocker.kicad_sch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]
2023-02-12 Added 23A PSU
    [FringeLocker.kicad_sch]
2023-02-15 V1.0 docs and 3D files
    [Assembly.skp, BOM.xlsx, FringeLocker.csv, FringeLocker.step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]
2023-02-16 Added PiezoDisc 3D supports
    [ClampPiezoDisc.stl, PiezoAssembly.skp, PiezoBase.skp, PiezoClamp.skp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]
2023-02-16 Reorg of folders
    [BOM.xlsx, FringeLocker-B_Cu.gbr, FringeLocker-B_Mask.gbr, FringeLocker-B_Paste.gbr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]
2023-04-19 V3.0
    Added a x10 gain stage and a 2nd order adjustable low pass filter
    Removed battery holders, requires external +/-15V to +/-18V supply
    [FringeLocker-B_Cu.gbr, FringeLocker-B_Mask.gbr, FringeLocker-B_Silkscreen.gbr, FringeLocker-Edge_Cuts.gbr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]

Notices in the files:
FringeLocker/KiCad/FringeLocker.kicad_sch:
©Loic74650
